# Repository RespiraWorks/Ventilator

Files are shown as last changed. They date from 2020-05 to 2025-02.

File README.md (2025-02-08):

# RespiraWorks Open Source Ventilator






</br>






This is a common repository for all hardware and software components of the RespiraWorks open source ventilator.

**If you intend to contribute, please read our [wiki](https://github.com/RespiraWorks/Ventilator/wiki) and [agreement](https://respiraworks.github.io/Ventilator/contributing/contributing.html).**

[RespiraWorks](https://respira.works/) is a 501(c)(3) non-profit organization with over 200 contributors worldwide working to design a low-cost and [open-source](open_source.md) ventilator for communities underserved by the global supply chain. Our objective is to provide the know-how and technology to enable local enterprises to manufacture and service these systems.

|           Most recent v0.4 rendering            |            Assembled v0.3 prototype             |
|:-----------------------------------------------:|:-----------------------------------------------:|
|  |  |

## Design Goals

We are dedicated to making this ventilator:
* [fully open source (software and hardware)](open_source.md)
* affordable (materials cost under US$2000)
* fully featured for extended clinical use through weaning and recovery
* vetted and filing-ready for regulatory review around the world
* optimized bill of materials to account for constrained supply chains
* designed for long-term clinical use beyond the pandemic

Most low-cost ventilator designs that have emerged in light of the COVID-19 crisis tackle the 'bridge' problem — keeping a patient alive for 6-8 hours of closely monitored care until they can be transitioned to a fully featured ventilator. We are designing that full ventilator, a highly valued medical device critical to care beyond the current crisis.

Our design shall provide essential features such as an intuitive, localized user interface, adaptive pressure- and volume-based operating modes, fine control of oxygen concentration, High Flow Nasal Cannula and other advanced features. What sets us apart from other similarly ambitious projects is our dedication to being fully open source. This repository embodies that promise.

We are targeting middle- and low-income parts of the world that will deal with COVID-19 for longer, with less access to healthcare, and a larger deficit of medical devices. We aim to deliver a design which meets the same operational rigors of current commercial ventilators, while addressing the high barrier to entry for such devices.

If you can lend your skills towards achieving this goal, please contact us at [join-us@respira.works](mailto:join-us@respira.works?subject=[GitHub]%20Join%20request). A list of roles we are looking to fill is also on our [website](https://respira.works/join-us).

## Project Status / Disclaimers

**This is an incomplete, as yet untested design that is not intended to be used on patients.**

**The repository contains live documents. There may be incomplete or contradictory information about various aspects of the design. Components may or may not connect and integrate as intended. Contents may also be out of date. If you decide to buy or build anything, do so at your own risk.**

We are currently in the process of designing our v0.4 prototype, plans whereof are captured in some of our outstanding [Milestones](https://github.com/RespiraWorks/Ventilator/milestones). The `master` branch of this repository includes bleeding edge changes in electrical, mechanical and software aspects of the project. Browse at your own peril.

For the latest stable and tested (but also obsolete) version of the design see the [Releases](https://github.com/RespiraWorks/Ventilator/releases) page.

## Repository Structure

* [**Documentation pages (outside of repository)**](https://respiraworks.github.io/Ventilator/index.html) - auto-generated pages (should eventually) include:
  * Requirements documentation
  * Regulatory documentation
  * Software documentation
  * Bill of materials for manufacturing
* [**Documentation source**](docs) - source files for the above pages
* [**System Design**](design) - describes the functional implementation and design theory of the system
* [**Manufacturing Design**](manufacturing) - describes the physical design of the ventilator and its components. Includes CAD models and notes on the manufacturing process
* [**Main Circuit Board**](pcb) - design, materials, assembly instructions for the ventilator main circuit board
* [**Software**](software) - source code for cycle controller and user interface, debug tools, and test scripts. Software architecture documentation is also here.
* [**Quality Assurance**](quality-assurance) - quality assurance strategy, testing plans, data

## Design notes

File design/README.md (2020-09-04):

# System Design

This section of the repository contains the description of ventilator design implementation and closure of issues which
apply at the system level, such as architecture configuration.

## Design Motivations

When approaching the design for the ventilator, we learned some features cannot be sacrificed if our ventilators were
to have a lasting impact for communities in need of advanced life support equipment. There are numerous avenues,
however, to reduce cost through tuning the performance specification to targeted use cases. This includes the ability
to ventilate high resistance, low compliance lungs at small tidal volumes and high respiratory rates. Our design can
significantly reduce the delivered cost of such a device by
1. reducing some performance requirements
2. developing software under a crowd-sourced model
3. not charging licensing or royalty fees.

The design has focused on a pneumatic implementation, where possible to avoid mechanical complexity (bellows, actuators,
etc), thereby placing more of a burden on the electrical and software design. This is informed by our experience that a
deep expertise of electronics is more globally prevalent than similar expertise in mechanical engineering. The device is
intended to be manufacturable by facilities that manufacture consumer electronics, automotive parts, refrigerators, or
other similar manufacturing entities near to the point of use. This approach allows flexibility in selecting
manufacturing partners who are supported from the engineering side by our globally distributed team of volunteer
engineers and manufacturing-quality professionals. To enforce this process, the design strives to identify solid supply
chain alternatives for each component and choose components that are easily sourced in our targeted regions of use,
such as Guatemala, India, Kyrgyzstan, or Nigeria.

The custom case, sensors, and valves are designed to use injection molded, laser cut, or sheet metal folded parts that
then require only basic tools to assemble, making them amenable to any number of manufacturing facilities around the
world. The chosen purchased components are readily available through global markets, including automotive supply
chains (e.g. valves and pressure sensors) and factory/warehouse supply chains (e.g. blower, tubing and pipe fittings).
The control and graphics board is designed around a custom PCB, but assembled using hand-solderable components if a
turnkey PCB supply chain were not available (though practically this would likely not be feasible from a QA perspective).

## High Level Design

The RespiraWorks Ventilator has four major subsystems with tightly
coupled interfaces:

1. [pneumatic system](pneumatic-system)
2. [electrical system](electrical-system)
3. [software system](../software/design) (documentation in code directory)
4. [mechanical assembly](mechanical) to enclose the device and provide structural support.

**#TODO:** Introduce all subsystems properly

The diagram below shows the conceptual interactions between the
pneumatic and electrical systems, with software running on both the main
controller (STM32) and a second independent graphics computer (Raspberry
Pi 3+/4) controlling the User Interface.

The following sections walk through this in more detail and explain the
basis for the design selection of various components.

Ventilator Functional Block Diagram
([source](https://docs.google.com/presentation/d/1ye96itSLfdbO9PQT0MSiq6xR2ArqD2MpV1Wj8ORfHeo/edit#slide=id.g7330d84036_1_0))



## Other Documents

* [Design rationales](design-rationales.md)
* [Concept of Operations](conop.md)
* [Systems modeling in Modelica](modelica.md)

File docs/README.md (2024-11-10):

# Documentation

The documentation created here is written in reStructuredTexT and generated using [Sphinx](https://www.sphinx-doc.org/en/master/) via a GitHub action.

## reStructuredText

reStructured text is similar to Markdown in that it is ASCII formatted text that is mostly human-readable and contains directives that specify how the text should be rendered in HTML, and other output formats.

reStructuredText is more complex than Markdown and allows for much greater flexibility in formatting as well as additional features such as *directives* that act like variables/macros that are defined once and expanded in place.

## Document Generation

The GitHub action rules can be found in `.github/workflows/docs.yml`

C++ API documentation is generated using [Doxygen](https://github.com/doxygen/doxygen)

## Variables

Frequently used values that may change can be defined in the `conf.py` file in the `rst_prolog` section. The `rst_prolog` gets including in every `.rst` file and the variables can be referenced by using the format `|VARIABLE_NAME|` which will get expanded into the generated text.

## Building the docs

Use the [docs.sh](docs.sh) script in this directory to install required dependencies and build the documentation.

To install all needed dependencies (do this once on your development machine):

```shell
./docs.sh install
```

To generate the documentation, run:

```shell
./docs.sh build
```

To render wiring harnesses only:

```shell
./docs.sh wire ./path/to/dir/or/file.yml
```

If the directories are polluted, and you want a clean slate:
```shell
./docs.sh clean
```

The generated output can be viewed by opening the file `docs/_build/html/index.html`, or you can run this script to have it open it up for you in your browser:

```shell
./docs.sh view
```

You can also check the validity of all links in all markdown and RST-generated files by running:

```shell
./docs.sh check
```

however, for this to work you must install the `lychee` tool, as described here: https://github.com/lycheeverse/lychee.
Otherwise, validity of links will be checked by CI scripts upon committing changes to the repo.

## Additional features and scripts

### Part purchasing tables

Parts catalog with links to vendors is generated by a set of custom scripts. The `json` file with parts definitions and relevant custom scripts are all maintained in [docs/purchasing](purchasing)

### Wiring assemblies documentation

Wiring assembly documentation is generated using the [WireViz](https://github.com/formatc1702/WireViz) tool. All wiring assembly definitions and relevant custom scripts are maintained in [docs/wiring](wiring).

### Traceability

We use a [traceability plugin for Sphinx](https://melexis.github.io/sphinx-traceability-extension/index.html) to generate requirement and test traceability reports.

A traceable item is defined using the `.. :item:: <id>` keyword.

By defining a traceability relationship in the target (ex. derived requirement
`:fulfills: <parent requirement id>`), and bidirectional link is created between
 the target and source `:item:`s. Traceability matrices and charts can be
 generated based on these linkages.

Over time, we can add additional attributes to the traceable items to trace data
 such as verification method, status, etc...

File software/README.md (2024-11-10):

# Ventilator Software

This directory contains the source code for the ventilator software, test code, sample data and debug utilities.

**DISCLAIMER: You should not use this on any living beings - as a ventilator, or in any other way.
These are utilities for bench testing with mechanical lung simulators only. It is also assumed that you are familiar with the software architecture and generally know what you are doing.**

## Contents

* [bootstrap](bootstrap) - initial deployment scripts for all software directly via the Raspberry pi integrated in a ventilator. Can also be used to configure a linux machine for software development or integration testing.
* [design](design) - documents on software architecture and requirements
* [common](common) - code common to both controller and GUI executables
* [controller](controller) - code for pneumatic system controller (stm32)
* [tools](tools) - controller debug client and other tools for calibration, configuration and testing
* [gui](gui) - code for the ventilator graphical interface (Qt)

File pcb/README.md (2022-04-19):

# Ventilator Mainboard 

This directory contains files for the Ventilator mainboard design.



The RespiraWorks Ventilator Mainboard PCB is a custom component that integrates the Cycle Controller, UI Computer,
sensors, actuator drives, power supplies, filtering, and protection components.

Due to the coupled nature of the controls, electrical, and mechanical components and their design the RespiraWorks
ventilator contains a custom fabricated printed circuit board (PCB) to connect the microcontroller, interface processor,
and sensor interfaces. The use of a custom PCB greatly reduces the chance for electrical assembly and fabrication errors
and is far more amenable to a quality fabrication process than hand-soldered components. We do not intend for this
component to be hand-assembled, and engineering turnkey fabrication instructions have been generated as part of the
submission; no assembly instructions are provided here.

The original Rev 1 PCB was done in Altium.  As of Rev A, this project has moved to KiCad for better accessibility.

## Rev A

The latest revision of the PCB is Rev A, designed to be used in the top-level design revision Ventilator v0.4.

The main design is in this folder and the project file is here: [Ventilator Mainboard Rev A](Ventilator.pro)

Recently exported files for PCB manufacture can be found on our Google Drive at
[Manufacturing/Output files v0.4/PCB](https://tinyurl.com/2p8af3fm).

This revision integrates many of the modules and daughter-cards in PCB Rev 1.0 into a single PCB, while breaking out the sensors to daughter-cards to make it better adaptable to sensors available in other markets.  It adds some important new features:
 - Moved CycleController from STM32L452 to STM32L496 microcontroller for more I/O pins, memory, and storage.
 - Added an independent FPGA-based supervisor.
 - Higher power capability now up to 120W.
 - Self-powered power loss alarm.
 - Integrated stepper drivers.
 - Ambient pressure sensing for altitude compensation.
 - Real time clock capability.
 - EEPROM for storing calibration data.
 - Additional pressure sensor channels to enable nested flow control.
 - Temperature sensors to monitor component health.
 - Integrated Li-Ion battery backup, charging, and monitoring.
 - Additional power connections for display, fans, and indicator lights.

## Sensor daughter-boards

> TODO: add documentation about these

## Rev 1.0

An archive of the previous version of the PCB, including the Altium-based design project and a snapshot of the old
readme is available on our Google Drive at
[Manufacturing/Output files v0.2-0.3/PCB](https://drive.google.com/drive/folders/1xHPLvo59tGI5uU38FrWMkVGmK_UR2sjQ?usp=sharing)

## Current issues

Issues for PCB work are tracked by tickets with the [PCB label](https://github.com/RespiraWorks/Ventilator/labels/pcb).

Somewhat related are the [Electrical design](https://github.com/RespiraWorks/Ventilator/labels/Electrical) issues.

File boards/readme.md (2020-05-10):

This directory holds the board file used by platformio to build the stm32 controller software.

The board file (custom\_stm32.json) was copied from the platformio board file nucleo\_l452.json .platformio/platforms/ststm32/boards/nucleo\_l452re.json

The main difference being the removal of the variant line to prevent platformio from including the stm32 supporting HAL.

Additionally, a few additional files related to the stm32 build have been added to this directory as a convenient place to keep them:

stm32\_ldscript.ld - This is the linker script copied from: \~/.platformio/packages/framework-arduinoststm32/variants/NUCLEO\_L452RE/ldscript.ld with some minor changes such as removing the heap (not used) and stack (defined in the HAL cpp file).

stm32\_scripts.py - A short Python script used by the platformio build to add some linker flags that can't be added in the platformio.ini file.

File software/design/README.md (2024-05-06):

# Software Design

The RespiraWorks ventilator includes software running on two computers:
an STM32 microcontroller and a Raspberry Pi.

Module diagram

The microcontroller runs bare-metal and controls the sensors and
actuators (valves and blower).  Its main loop runs every
10ms on a hardware timer interrupt,
and the code running in the main loop contains no loops of variable
length, ensuring minimal jitter. The microcontroller’s software is
written in C++.

The Raspberry Pi runs Linux and is used for displaying the GUI. The
software we wrote is a Qt app, also written in C++. The app displays a
GUI on the ventilator’s touch screen, showing sensor data received from
the controller. Users set high-level parameters via the GUI (e.g. "PIP
20 cmH2O"), and then the GUI software commands the controller to meet
these parameters. The GUI software is also responsible for calculating
alarms and readings derived from raw sensor values (such as measured
PIP/PEEP).

We chose to use two separate computers for three reasons.
1. Two computers reduces the amount of software that is immediately hazardous
to the patient. Since our UI code runs on a separate device with no
direct access to the ventilator’s actuators, a bug or crash in it is
less likely to cause immediate harm; the ventilator will just keep
running with the most recent parameters (and, in the future, sound an alarm).
2. This design saves time and money because it allows us to use
large libraries like Linux and Qt, which make it easier to develop the
GUI, but would likely be unacceptable in a patient-critical module like
the cycle controller.
3. Having two modules adds a level of
redundancy. If the microcontroller crashes, it will immediately receive
new commands from the Raspberry Pi, and the Pi can raise an alarm.
Similarly, if the Pi crashes, the ventilator continues running with the
last set of parameters, and the cycle controller can raise an alarm.
(Disclosure: Neither of these alarms is currently implemented, and we
have not performed extensive testing of this failure model.)

Like the rest of the RespiraWorks project, our software is developed in
the open on GitHub. We have an extensive continuous integration
infrastructure running unit tests on x86, and we are building
infrastructure to run automated tests on the full device. We are also
nearly ready to start testing our software against a Modelica simulation
of the device. We hope this will make it easier for developers who do
not have access to hardware to contribute to the project. We also
believe having a robust simulation environment will allow us to run
tests that would otherwise be prohibitively time-consuming, for instance
running each commit against many combinations of ventilator parameters
plus lung compliances.

Besides a detailed user manual and maintenance plan, the device will also
come with a robust self-test mode.  This ensures that produced
ventilators achieve necessary safety levels before they are used with
patients and will allow users to check the health of the device over its
lifetime. A cryptographic hash will be released with the approved
software, and allow local manufacturers to be confident in the software
they are loading to the device.

## Communication Between Pi and Microcontroller

The microcontroller and Raspberry Pi communicate over a serial bus using
a simple, predictable protocol. Every ~50ms, the microcontroller sends
its current state to the Raspberry Pi, and every ~50ms, the Raspberry
Pi sends its full state to the microcontroller.  There are no ACKs,
resends, detection of missed packets, etc.

This simplified communication protocol avoids failure modes present in
other protocols.  For instance, imagine a different, stateful protocol
where one command the GUI can send is `set PIP to X`.  Suppose the GUI
sends two packets, `set PIP to 15` and `set PIP to 20`, and imagine that
the first one gets corrupted or lost on the wire.  The controller must
not accept the `PIP 20` command until it receives and applies the `PIP
15` command, otherwise the final PIP will be 15!  This requires buffers,
resends, and complex logic that, in the limit, looks much like a full
implementation of TCP.

Our design sidesteps this whole class of problems. If a message gets
missed or corrupted, we can just wait for the next one.

The state is encoded for transport on the wire using protocol
buffers (specifically, nanopb) and
wrapped in a frame with a checksum for detecting packet corruption. As
compared to a fully custom binary format, this makes it far easier to
change the protocol and potentially interoperate with other systems.

## Software component architecture

[Controller architecture](controller_architecture.md)

[GUI architecture](GUI_architecture.md)

## Other documents

There is a document defining the [ventilation modes](ventilation_modes.md) we intend to support.

## Testing considerations

There is a strategy defined for [embedded software testing](embedded_software_testing.md).

## Milestones

We have completed and successfully demonstrated the
[Alpha Milestone](milestone_alpha.md) and the [v0.2 milestone](milestone_v0.2.md).

## Design Reviews

**TODO:** Links to the design reviews

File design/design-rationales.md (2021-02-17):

# Design Rationales

NOTE: The documentation below is a summary and may be out of date.

## Overview

This file is meant to document the rationales for the design decisions we're making - or things we considered and rejected.

Caution: this document has not been formally reviewed and is a work in progress. Be responsible to
understand the provenance of documentation.

Also note: right now we are collecting initial information here since it is easier - we may split
this up to have the different sections live with the different component folders, but we'll figure that out later.

## Guiding Principles

1. **Low cost but robust and safe** - we want to create something that is affordable, but also that can perform the
necessary duties reliably with high confidence over extended periods of time. The goal is to satisfy external
specifications for ventilator requirements - but also assess the cost of the requirements and not blindly follow them if
it drives big decisions in the system.

2. **Keep It Simple (Stupid)** - remove complexity wherever possible to reduce failure modes (and cost), without
sacrificing key functionality (though certain functionality may not be achieved)

3. **Make it something that doctors will use** - it won't necessarily do everything, but we want the ventilator to
provide the key needs of doctors. Therefore, we must keep doctors extremely in the loop and constantly get feedback from
them on what we're doing.

4. **Amenable to developing world supply chains and maintenance** - don't presume that the medical context we might be
used to is the same in our target market. The only way to get this information is contact with doctors and workers
familiar with the facts on the ground.

5. **Open source** - we want this project to be something that anyone who wants can build off of and leverage.
Therefore, all designs, rationales behind those designs, requirements, processes, etc. will be documented in a common
repo that everyone has access to. **#TODO** - go through and make sure all of the links in here are in git so that
people can access them (some slack links exist temporarily before the information is fully resolved and moved to git).

## System CONOPS/System Design

More detailed thoughts on this [here](conop.md).

* Targeting **pressure control** for two reasons:
    1. We got early feedback that this was most important to doctors - though we have gotten feedback that volume
       control is also important.
    2. A lower cost pressure controlled system seemed more achievable - and theoretically a good pressure controlled
       system should be able to do volume control. Currently we are pursuing pressure control and will be evaluating how
       accurate volume measurements we can get to determine if the design can also support volume control.

* **Doctors need fine control of FiO2** -> this drives the need for an oxygen supply, the need to support oxygen mixing
and sensing, and the need for a variable state valve on the O2 supply to adjust the flow rate dynamically.
**#TODO** Need more info on the ox system design we pick.

* **Multiple closed loop (feedback control) systems create complexity by creating interacting dynamics** -> we're
attempting to only have a single closed loop controlled part of the system at a time and to target one key feature (e.g.
pressure with FiO2 achieved across cycles). We're also working to determine which components (e.g., valves, blower) need
to be controlled and how in order to figure out what will actually support the system requirements.

* Anything that will be exposed to high oxygen concentrations and pressures needs to be safe and ox-clean. This drives a
desire to **reduce the number of items directly in the flow as much as possible**, especially for high-pressure (greater
than 1 bar O2)

* **Air valve after the fan/blower with air valve being closed loop controlled and fan being open loop** -> The
ventilator requires a high rise time of the pressure when transition from PEEP to PIP. A motor which can change the fan
inertia this quickly against increasing pressure ends up being the fan for some high-performance ventilators, or
expensive. We have solved this by the use of a proportional valve after the fan. The fan runs at constant power, and the
pinch valve is used to modulate the flow. For reference, one fan we got quoted was $500 and we were never able to get one
delivered. A fan capable of meeting the pressure spec + an air valve capable of the rise time spec was less than $75.

* The goal is to maintain **some bias flow through the system at all times**, both to help the fan and to avoid big
surges from completely opening and closing different parts of the circuit. This also helps ensure a 'one way' flow of
particles and aids with sterilization.

* **Trigger breath transitions off of changes in flow instead of pressure** -> Because the ventilator is pressure
controlled, it adapts to small changes in pressure by adjusting the flow rate (by adjusting the valve states) in order
to maintain pressure. Therefore, changes in flow rate are a better sign that the patient is attempting to inhale or
exhale. **#TODO** need to confirm this/flesh this out as we go

* **Anti-asphyxiation design** (**#TODO** need to confirm all this)
    * **Pneumatic** If the ventilator loses power, it is important that the patient is able to breathe and is not given
      dangerous amounts of pressure/flow. The oxygen system is fed by an external pressure source that the ventilator
      doesn't control; therefore, in the loss of power it is important to shut off flow from the oxygen system to keep
      the patient safe. We accomplish this by using a normally closed solenoid on the oxygen limb. The air/blower valve
      and the exhale valve are made to be normally open so that those paths are unobstructed to allow the patient to
      breathe.
    * **Electrical** To support the air/blower valves and exhale valves being normally open, the Cycle Controller
      watchdog timer is connected to the stepper motor drivers, which will default them to an unpowered state in the
      event of a Cycle Controller computing failure, causing the valves to snap open.

* **Use of stepper motors** - **#TODO** need to fill this out

* **Metric vs imperial** - **#TODO** fill this out when we make a decision

## Valves

* **Pinch Valve (Custom design)**
    * Low cost, robust design for achieving variable flow based on peristaltic tubing.
    * The valve mechanical components are not exposed to the flow, which means it is not exposed to high O2
      concentrations directly.
    * Normally open, which is important for anti-asphyxiation in the case of power loss
    * Still evaluating fatigue and lifetime / sealing.
    * Originally designed as the exhale valve to give control for maintaining PEEP - under considering to use for both
      the air inlet and for the oxygen inlet
    * For more informatin about the design of this valve, see [here](../manufacturing/internals/pinch_valve)

* **Idle Air Control Valve (IAC)**
    * Common automotive part that is cheap and widely available.
    * A linear stepper motor drives a pintle up and down to create a variable orifice.
    * Unclear how these valves perform in high O2 environments or if they could be sufficiently rated/cleaned.
    * Significantly cheaper, more robust, and more widely available than the pinch valve.

* **Proportional Solenoid (PSOL)**
    * Relatively uncommon part but used in traditional ventilators.
    * Provides precise, reliable control of high-pressure gasses.
    * May be cost effective but requires a high-pressure source of oxygen (can not use low pressure sources like oxygen
      concentrators without a booster pump).
    * O2 cleaned PSOLs are relatively hard to find, though are already in use on ventilators. We may be able to clean
      automotive PSOLs.
    * Normally closed, which is important for anti-asphyxiation. **#TODO** need to confirm this

* **One way valve (check valve)**
    * Needs to work in an O2 environment
    * Needs to be reliable and relatively low cost
    * Still figuring out the exact one way valve design
    * Two possibilities are a normal umbrella seat check valve, problem is these have a high cracking pressure. This
      could be OK on the intake side where the fan can generate this but would be a problem on exhale.
    * duckbill valves have also been explored, but these can chatter at low flow rates.
    * Could possibly modify a normal check valve by cutting the spring down or out.

* **Relief Valve**
    * **#TODO** when we figure this out

## Tubing
* Pick peristaltic tubing in the pinch valves so that it can withstand many cycles
* Otherwise any biocompatible tubing is fine, gneerally Tygon for most of the testing.
* Needs to be O2 safe
* 3/4 inch standard allows relatively cheap fittings. Need to transition to metric for int'l.

## Sensors

* **DP sensors / Venturi**
    * The goal of the venturi design is to measure the flow through the system at a limited pressure drop and with a
      large signal.
    * Venturi's are nice because they are cheap and yet can provide reliable flow measurements. See
      [this ticket](https://github.com/RespiraWorks/Ventilator/issues/9) for info about evaluating the venturi's.
    * Currently we are using the difference between the two flow measurements (one for inhale and one for exhale) to
      determine the tidal volume delivered to the patient. We are still evaluating how to do this - see
      [this ticket](https://github.com/RespiraWorks/Ventilator/issues/57) for more information.
    * Another open questions is manufacturing of the venturis - currently the goal is to design a venturi that can be
      injection molded.
    * For more informatni about the venturi design, see [here](../manufacturing/internals/venturi).

* **Patient Pressure sensors**
    * Needs to be reliable, handle many cycles, and meet the required ranges and accuracies of the requirements
      (**#TODO:** flesh this out more).
    * Currently only one sensor is used, but maybe a second one is required for reliability.

* **O2 sensor**
    * The O2 sensor needs to be able to measure up to 100% O2
    * Right now we are using a galvanic cell O2 sensor - but those are known to degrade quickly.
      [This ticket](https://github.com/RespiraWorks/Ventilator/issues/56) is tracking our discussions on this topic.

* **Mass flow sensor***
    * We have shied away from mass flow sensors because they are very expensive when compared to the DP sensor/venturi
      design. However, they are accurate and used on other system so they are not completely ruled out.

## Filters
* Filters on inlet/outlet to prevent contaminents from the surrounding environment getting into the device
* Filter on patient circuit to avoid device contamination and spreading particles between patients
* We're currently looking at HEPA filters since they are commonly avaible and cheap - but we're also evaluating other
  options. HEPA filters are appropriate because they are designed to filter small particles.
  [More info on HEPA filters](https://ntrs.nasa.gov/archive/nasa/casi.ntrs.nasa.gov/20170005166.pdf)
* 2 part mold for holding the filters is meant to be easily manufacturable and to allow easy changing of the filters
  over time
* Filters are placed physically on the outside of the box so they can be replaced without the box being opened

## Blower
* Current blower is not rated to 100% O2, which drives the lack of a blower on the O2 system and a one way valve in
  front of the blower to keep it separate from the high O2 part of the system.
* We have evaluated a large number of blowers. When balancing supply chain, ubiquity of specification, and future
  availability, we settled on this one. However, there is an issue with the pressure spec for the fan. If we needed to
  reach 60 cm H2O, this fan might be under powered. We are currently leaning to not support those high pressures
* **#TODO:** link to the fan we picked

## Enclosure
* Must be sterilizable
* Must be manufacturable with commonly available fabrication equipment in the markets we are assessing (currently
  targeting custom folded sheet metal)
* Enclosed to protect the internals and keep out dust
* Has an external fan for cooling the internal electronics
* Ruggedized and compatible with the hospital environment
* Must support easy assembly and maintenance of the various components

## Humidifier
* Currently planning to use an off the shelf external humidifier—see [this ticket](https://github.com/RespiraWorks/Ventilator/issues/704) for more details.

## PCB/Electronics

* **SRM32 Microcontroller For the Cycle Controller**
    * More powerful than the simpler arduino and Raspberry pis, but still cheap and widely available
    * Used in other medical devices
    * Comes with more powerful/extensive debugging tools
    * Familiar to many of the members of our team
    * See [this ticket](https://github.com/RespiraWorks/Ventilator/issues/709) for more details on why a STM32
      microcontroller was chosen.
* **Rasperry PI and Rasperry PI Touch Screen for GUI**
    * Cheap and widely available
    * Existing libraries for touch screen interactions that can be leveraged
    * Has lower performance requirements than the cycle controller
* **Power Supply**
    * 12V standard chosen to ensure flexibility of power supplies (e.g. battery or UPC)
    * Open question on internal alarms battery
* **#TODO** - need more here.
* **#TODO** - add diagrams from design reviews and such

## Software

* **#TODO** - add diagrams from design reviews and such
### Separation of UI Controller and Cycle Controller
* To maximize safety, it is important to minimize the amount of software that is immediately hazardous to the patient
  (can cause harm in <1s, making human intervention useless), and expose any hazardous software to high levels of
  verification and testing. By moving the UI code to a separate porcess, it reduces risk and saves time because the
  complicated UI code doesn't have to be exposed to the same verification and testing as the cycle controller.

* NOTE: Neither of the controllers are a complete backup for the other - this is not a redundant system.  If either
  fails in a way that is not fixed through the watchdog reset, an immediate intervention will be needed to keep the
  patient alive.  The objective in the case of either failure is to sound the alarm so that the intervention can
  happen - and to design the system such that in the event of a failure there is time to make an intervention.  Making
  a truly redundant system will add cost and time, and so has been deferred for now.

* **Watchdog Timers**
    * In the event of a computing failure in either the UI Computer or the Cycle Controller, a watchdog timer monitors
      each and will reset the offending computer, which should then be able to regain control of the valves.
    * **#TODO** it will need to be confirmed in the final design that the UI Computer cannot command any modes that will
      cause the Cycle Controller to hold these valves closed.

### GUI / UI Controller
* **#TODO** - needs more
* Items that fall within the UI Controller:
    * Cycle Controller Watchdog/Alarm
    * User Parameter Setting
    * Ventilation Mode Setting
    * Sensor Data Reporting
    * Respiratory Cycle Plot Display
    * Alarm Information Display
    * Alarm-specific alert sounds

### Cycle Controller
* **#TODO** - needs more
* Items that fall within the cycle controller:
    * UI Computer Watchdog/Alarm
    * Closed-Loop Valve Control
    * Open-Loop Blower/Valve Control
    * Respiratory cycle Control
    * Sensor Data Reading
    * Sensor Failure Alarm
    * Overpressure Alarm
    * Respiration Rate Alarm
    * Broken Loop Alarm

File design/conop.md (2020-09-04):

# RespiraWorks Ventilator Concept of Operations (conop)

## Purpose

- Build a common understanding of ventilator internal operation amongst different parts of the team.

- Caution: this document has not been formally reviewed and is a work in progress. Be responsible to understand the provenance of documentation.

## Document Content

- Summary of key constraints
- Understanding of current intra-breath cycle control for the development ("Pizza") board.
- Preliminary description of system operation for next iteration of system with O2 mixing
- Envisioned Inter and Intra-breath cycle control states
- Open questions / points to resolve.

## Functional Diagram

Functional Block Diagram

## "Pizza Build" Intra-breath Cycle Control

The Alpha system flow path is:
- Fan
- Air Valve (not on current pizza build)
- Tee <-> Test Lung
- Exhale valve
- Exhaust

The Alpha build (first iteration) did closed loop control on the blower speed and setpoint control on the exhale valve state to achieve the desired target pressure. However, this left significant shortfalls in both pressure rise and pressure reduction times.

The intra-breath control cycle for the Alpha build is:
- **Inhale:**
    - Increase pressure set point for closed loop control to PIP pressure
    - Exhale moves to exhale position (fully closed)
    - Controller adjusts blower speed based on PID control closed around the measured patient pressure
    - PIP pressure target is maintained for a specified amount of time - then step transition to exhale
- **Exhale:**
    - Exhale valve moves to exhale position (fully open)
    - Controller adjusts pressure set point for closed loop control to PEEP pressure
    - Controller adjusts blower speed to meet PEEP.
    - PEEP pressure target is maintained for a specified amount of time - then transition back to inhale

Alpha build has no inter-breath or "adaptive" control on top of this.

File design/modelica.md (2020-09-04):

# Modelica Simulation Model

## Modelica Overview

Modelica [www.modelica.org](http://www.modelica.org)
is a non-proprietary, object-oriented, equation-based language used to model complex multi-domain physical systems.
Developed by the non-profit Modelica Association, the Modelica language is widely used in industry for modeling physical
systems with mechanical, electrical, pneumatic, hydraulic, thermal, control, electric power, and process-oriented
components.  With Modelica, models can be built from the open source Modelica Standard Library (the largest free library
for multi-domain models), other open source libraries, commercial libraries, and custom in-house libraries to leverage
existing modeling technology while providing the openness and flexibility to incorporate custom modeling IP.

Modelica is used for modeling the dynamic behavior of technical systems.  Models are described by differential,
algebraic, and discrete equations.  Modelica physical models are acausal and allow the creation of reusable primitive
components, subsystems, and complete systems.  To illustrate a simple Modelica model, the figure below shows the
graphical representation and Modelica code for the 1D rotational inertia from the Modelica Standard Library.  Modelica
models are written as equations, typically in standard text book form, that express relationships between variables.
Since Modelica models are descriptive but not necessarily programmatic, a Modelica tool is needed to generate executable
code.  The entire process starting from Modelica code to a simulation result is shown in the figure below. A Modelica
compiler assembles the Modelica code, performs symbolic manipulation on the equations, generates C code, and compiles
the C code into a simulation object that is linked with a numerical solver that executes to generate the simulation
result.  Both open source and commercial compilers are available for Modelica.  With the powerful symbolic processing
from a Modelica compiler, modelers are free to focus on developing high quality models for systems engineering rather
than numerics and equation solving.

## Model Overview

For the ventilator work, we partnered with Modelon, who provided licenses for a beta version of their commercial
Modelica tool Modelon Impact [https://www.modelon.com/modelon-impact/](https://www.modelon.com/modelon-impact/).
Modelon Impact is a fully featured Modelica development and simulation environment integrated into a web browser.
Modelon Impact is designed to enable system simulation beyond just CAE experts and facilitate collaboration and
model-based engineering.

Modelon helped us to develop a package of models to support the ventilator physical system and controls development.
These models are based on Modelon's Pneumatics Library, a commercial library for modeling pneumatic systems.  Modelon
continues to develop the ventilator modeling package in partnership with RespiraWorks.

As shown in the figure below, there are three main parts of the model: the controller, the ventilator, and the patient.
The beauty of modelon impact is that it lets you easily swap in different instances of each of the components and see
how that affects your results. Below we'll walk through how each of these were created.

Screenshot of Modelon Impact Showing The Model GUI



### Patient

There are currently three main different patient models. The first is a basic model that allows the user to specify a
resistance and compliance and then calculates the internal volume and pressure based on pressure and flow rate from the
ventilator. The second is a breathing model that allows a respiratory rate, IE ratio, and a musculatory pressure to be
specified, controlling both how quickly and how forcefully the simulated patient breathes. There is also a more advanced
lung model that incorporates more parameters to enable more complex simulations, though we have not used this model
extensively yet.

### Ventilator



 Current Ventilator Model in Modelica

As the ventilator design has changed, there have been many iterations of the ventilator model in modelica. The most
recent one is shown in the figure below, where you can see the oxygen leg with oxygen source and ox valve, the air
inhale branch with blower and pinch valve, the patient circuit with venturis before and after, and the exhale leg with
the exhale pinch valve. The control signals from the controller enter through the control bus at the top and are then
routed to the actuators (blower and 3x valves), and the pressure measurements are passed back to the controller through
the same control interface.

Each component is built up using the modelica language. The components in this ventilator model are a combination of
default modelica components and components created specifically for our ventilator. The blower component, the
proportional pinch valve components, and the oxygen valve components are based on test data and data sheets for the
actual hardware we are using. An example of the flow curves inside the modelica model for the custom proportional pinch
valves are shown below. Similar curves were created for the blower and the oxygen valve.



Flow Curves for Custom Proportional Pinch Valves Used Inside Modelica, Based on Flow Testing. Valve flow vs opening
command with different curves for DP across the valve.

### Controller

We explored two different ways of implementing a controller in Modelica. The first was to build the controller in
modelica, using components based in the modelica language. The second is to write a controller outside of modelica
(e.g. in C++) and to then link it through the modelica interface. The first approach allows rapid interaction for those
who are less familiar with how to implement controllers in software; this allowed us to prototype different controller
configurations before we actually had the hardware set up to test them with the real system. The second approach could
be useful for testing the controller software without being constrained by hardware, something that is discussed in the
next section.

### Executing The Model

When the model is run, the various components begin in their initial state. The tool then steps forward in time,
calculating both the commands from the controller and the corresponding response of the system at each time step,
solving the various underlying equations to calculate pressures, flow rates, etc. The results can then be visualized to
see how the system performed over time.

## Comparing Model to Hardware

Currently, we are working to verify that the model matches what we see with hardware. This has been challenging for a
few key reasons:

*   Rapidly changing controller code that hasn't been integrated into the modelica model. This makes it difficult to
    tell if differences between results from the model and the hardware are because of issues in how the hardware is
    modeled, or differences in the commands coming from the controller, which affects the system response.
    Unfortunately, the structure of the controller code has also been changing, which means that this isn't completely
    solved by using the external controller.
*   Rapidly changing hardware that has not been completely characterized. As we iterate on the hardware design, we have
    been changing components faster than we've been able to collect characterization data with which to anchor our
    modelica models.

Moving forward, we are evaluating ways to anchor the modelica model to give us more confidence in its predictive
capabilities.

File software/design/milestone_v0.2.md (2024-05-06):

# This milestone is complete

_Information below only for posterity._

## How to use this page
This is a high-level overview of what we want to achieve for v0.2 (a.k.a Covent) milestone. Up-to-date state of its implementation
is [here](https://docs.google.com/document/d/1CHgz-y6wV6duTg66s1h8-wZZ6Tn22U1iL5WtjhSYQgk). Requirements are captured on Valispace.

## Date

Deliver to Covent by June 18th.

# Objectives
## Modes
 1. Pressure Assist Mode. That is mandatory ventilation together with inspiratory attempt detection.
 2. (stretch goal) High-flow nasal cannula (HFNC). Ventilator provides light continuous positive pressure, patient breathes on their own.
 3. (stretch goal) Pre-test mode (a.k.a. self-test mode).

Full description of all ventilator modes is [here](ventilation_modes.md).

## User Interaction

See [UI Requirements](UI_requirements.md).

## Alarms
We need 6 alarms that were in covent requirements:
1. Gas pipeline failure
2. Pressure exceeds
3. Apnea
4. Pressure not achieved
5. Tidal volume
6. Electricity supply failure

## GUI
Two new features have to be added for Covent:
1. Modes selection
2. Alarms settings

# Requirements

Requirements are captured in Valispace, tag v0.2

# Tasks
Specific tasks are captured as GitHub Issues in the following milestones:
 - [v0.2 GUI](https://github.com/RespiraWorks/Ventilator/milestone/12)
 - [v0.2 Alarms](https://github.com/RespiraWorks/Ventilator/milestone/11)
 - [Pressure Assist Mode](https://github.com/RespiraWorks/Ventilator/milestone/8)
 - **HFNC mode** - deleted milestone (August 2020)
 - (stretch) Self-test mode - deleted milestone (January 2021)
 - (stretch) [v0.2 Controller](https://github.com/RespiraWorks/Ventilator/milestone/13)

# Brain dump, to be sorted and reorganized into sections above

We also need:
* Architecture / preliminary design review
* Calibration tools/modes for subsystems
* Validation testing plans for specific subsystems (this might be software or additional documentation overhead)
* Listing and managing the software-specific risks (note: this work is underway [here](https://docs.google.com/spreadsheets/d/1p26b3XyhEte8BvnE9otj118MW5ajGM21dGfTXldG8sM) by jam@)
* We need a software architecture review
* We need 1 or 2 people to help physical design team publish their content on github and document things in a colleague- and people-friendly way

Specific software designs needed:
* A design for alarm management ([Slack thread](https://respiraworks.slack.com/archives/C0100SF3N5T/p1589153203185000))
* A design for controller self-test mode ([Slack thread](https://respiraworks.slack.com/archives/C0100SF3N5T/p1589153203185000))
* Persistence (what to do if controller resets - start from blank slate? recover control state?)

## Robust testing and debugging
* A debugging interface - ability for developers to debug what's going on in more detail than the user-facing GUI provides
* Continuous Integration that runs tests on a real device:
  * Running unit tests against a device - which is also critical for validating the correctness of the HAL
  * Running integration tests against a full ventilator assembly
* Continuous Integration that builds a GUI image for RPi

## Simulated testing

We need simulated integration testing of physical scenarios such as "patient is hooked up" etc.

We have a sub-team of folks from Modelon who hang out on [#modelica](https://app.slack.com/client/T0102KRCH5M/C011HUP75EJ) and build a model of the system (ventilator + patient + controller) in Modelica, a language for simulating physical systems. We want to integrate our Controller with that model so we can simulate what would happen if the real ventilator was being controlled by it. See [these meeting notes](https://docs.google.com/document/d/14lrTVcYuuUii7QTvuJJneex-_uKSHQ33Hg9CR5pOARo/edit#heading=h.cpwphjtw2hj8) for more.

Can we check in regularly against Modelica to gain confidence that we're meeting functional requirements?

Contact persons:
* On Modelica side, John Batteh and Elizabeth Hillstrom.
* On Software side, Eugene Kirpichov

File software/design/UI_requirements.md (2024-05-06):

# User Interface Requirements

The UI runs on a 1024x600 touchscreen. There are no external buttons or anything.

The UI requirements below come from several sources:
* Original mock-ups (the black-and-white mockups included
  [here](https://www.ics.com/blog/ics-joins-respiraworks-on-ventilator-project))
* [ICS prototype](http://demo.ics.com/ventilatorui-demo/) that was built based on the mock-ups
* [This paper](https://ccforum.biomedcentral.com/articles/10.1186/s13054-016-1431-1) and
  [this demo](https://www.youtube.com/watch?v=BT3snJ1Hm2s)
* [These notes](https://docs.google.com/document/d/1QFFcg2gL3PXXzyqgSBz3XZQm_oobZ2osFuErh492UEA/edit) from a
  conversation with a respiratory therapist

The list below is incomplete and possibly wrong in some ways.
Please consult SRS [Requirements page](https://respiraworks.github.io/Ventilator/software/SRS.html).
However, Valispace also does not have complete information at the time of writing. Proceed with caution.

## Self-test mode

On startup, ventilator is in self-test mode. It performs a set of checks and reports on the status.

Some checks are **automatic** _(eg that a certain tube is not blocked: turn on the blower, check that output flow
sensor detects some flow)_, Some are **manual** _(eg for "the buzzer works" it needs to turn on the buzzer and ask user
whether it's audible)_

The **full set of checks** is not yet known and generally open-ended.
Checks should include **guidance on how to fix** if it failed.
The self-test mode should be easy to use _(the hospital where the therapist above works decided not to purchase vents
where it was too cumbersome)_.
Results of self-test should be retained in memory.

**Open questions:**
* Should you be able to perform self-test only on startup or at any time?
* Should you confirm that patient is not connected?
* Should device refuse to operate if a check fails?

See also https://github.com/RespiraWorks/Ventilator/issues/307.

## Ventilation modes

We intend to support **Command Pressure** _(device commands all breaths)_, **Pressure Assist** _(device detects inhale
effort and helps that breath, but also initiates breaths if patient doesn't)_, **CPAP with O2 therapy aka HFNC** _(light
constant positive O2-saturated air pressure, non-invasive)_.

_Note: Different sources seem to indicate that pressure-controlled modes are going out of favor and volume control is
preferable (regular - not PRVC or VC+) - eg see
[notes](https://docs.google.com/document/d/1QFFcg2gL3PXXzyqgSBz3XZQm_oobZ2osFuErh492UEA/edit). But for v0.2 we're doing
pressure control._

**Mode parameters**: Each mode has several parameters defining it, e.g. Respiratory Rate, PIP (Peak Inspiratory
Pressure), PEEP (Positive End-Expiratory Pressure), FiO2 (O2 percentage). Parameter changes must be confirmed before
taking effect.

**Displayed measurements**: In each mode we display real-time graphs and sensor readings of several measured values:
pressure, flow, volume.

**Measured vs. commanded values**: All or almost all values have a "commanded" and "measured" value. E.g. ventilator
tries to achieve a certain PIP - this is the "commanded" value - but what it actually achieves is the "measured" value.
If they're too far off, this is bad and usually triggers an alarm.

## Alarms
**Alarm formats:**
* https://docs.google.com/document/d/1bMZfkq_p8dkg7F0ZGVIFhityv-s3GVRMsm_Nd1zNlww/edit#heading=h.yvoratpyj4xl
* Specifies visual flashing frequency / duty cycle
* Specifies auditory pulse frequency / pattern
* Derived from 60601-1-8

**Alarm conditions:**
The main alarm types for v0.2 are **"measured value too far from commanded value"** and **"the device is in a bad
state"** _(eg some tube disconnected, battery low etc)_.

Consider a **"check settings"** alarm. Per
[notes](https://docs.google.com/document/d/1QFFcg2gL3PXXzyqgSBz3XZQm_oobZ2osFuErh492UEA/edit) drs check settings every
3-6 hours, so maybe we should issue a low-prio alarm if settings haven't been confirmed in longer than that.

**Alarm presentation:**
* Alarms are indicated visually and sometimes audially (buzzer, continuous tone).
* A good way to display the "measured value off" alarm is to color the wrong value's background.
* At any moment the GUI must display the highest-priority alarm.
* You should be able to see all active alarms

**Alarm priorities:** low, medium, high (buzzer), and one or two alarms emit a continuous beep.

**Alarm lifecycle:**
* The alarm becomes active when its condition is met.
* Open question: We haven't figured out a general rule for when an alarm stops being active.
* Alarms can be suppressed in several ways: eg. cancel a particular alarm _(we don't know exactly what this means)_,
suspend all audial alarms for 2 minutes, etc. (see `01_Alarms` in Valispace)

**General advice:**
* Alarm fatigue is real. Need to make alarm management simple and conductive towards minimizing fatigue.

**Additional alarms per ISO 80601-2-12:**
(See [Slack thread](https://respiraworks.slack.com/archives/C011UMNUWGZ/p1591500042061800?thread_ts=1591207530.031400&cid=C011UMNUWGZ))


## Event logs (not in v0.2)

GUI must include a way to view the event log. It must include:
* All alarm-related events (activated, cancelled etc)
* Confirmed parameter changes and mode changes

## Non-functional requirements
The screen resolution is 1024x600.

**Remote observation/control**
* Things must be **visible from a distance of N meters**. The Covent reqs say from 1 meter, but per
[notes](https://docs.google.com/document/d/1QFFcg2gL3PXXzyqgSBz3XZQm_oobZ2osFuErh492UEA) drs often want to observe
the screen from outside the patient's room, to decrease exposure to infection.
* Nice-to-have: remote control - also to decrease exposure.

**Usability:**
* Errors can kill a patient, and the UI is used by overworked staff. It is very important to design for minimizing
  chance of human error and minimizing dr fatigue.
* Staff in target markets where there's no vents will be inexperienced with vents. UI should help them, eg understand
  the numbers, guide towards configuring things right.
  * Example: in volume-controlled modes, there's an ideal volume of 4-8mL per kg of ideal body weight (based on
    gender/height). Could set default volume by that and color-code if setting outside this range.

Consider the likely working conditions - need a dark theme (optionally light theme too).

The UI should be colorblind-friendly, at least for elements where discerning the color is safety-critical.

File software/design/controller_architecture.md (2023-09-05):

## Cycle Controller

Our cycle controller runs on an STM32 ARM chip and is written in C++17.

For more details on the inner workings of the controller, see
[Controller description](https://docs.google.com/document/d/1hztIBu9DR52r0LQuIpt6DZByBLfXfJy21BGqk2F34g8).

**TODO:** Migrate contents of the above document to github.

There is a
[Circuit board ICD](https://docs.google.com/spreadsheets/d/1JOSQKxkQxXJ6MCMDI9PwUQ6kiuGdujR4D6EJN9u2LWg/edit#gid=0)
which is a good reference on controller peripherals.

### Why C++?

C is a much more common programming language in the embedded space, so
our choice of C++ deserves some discussion.

Simply put, we chose C++ over C because we believe it is a more
productive programming language.  Here are some advantages we’ve found
to using C++.

-   In C we’d have to represent a pressure measurement as a number, e.g.
    a float.  This is
    [error-prone](https://mars.nasa.gov/msp98/news/mco990930.html) in
    part because the compiler can’t help you keep your units consistent.
    In contrast, our C++ code represents a pressure measurement using an
    explicit
    [Pressure](../common/libs/units/units.h) type.
    You can create a Pressure from a measurement in kPa or cmH2O and the
    software will do the unit conversions automatically. We also support
    operators between types.  For instance, dividing a Volume by a
    Duration yields an object of type VolumetricFlow, again with the
    units automatically correct. This is a zero-cost abstraction -- it
    runs just as fast as the equivalent C code -- and it eliminates
    whole classes of bugs.\
-   We use pieces of the C++17 standard library to add safety to our
    code.  For instance, we use C++’s std::variant class for
    discriminated unions instead of C’s union construct.  We also use
    std::optional throughout the code to represent a value that may not
    be present.  This is much safer than most C solutions (e.g. using a
    sentinel value like -1 or NaN to mean "not present").
-   Some language features of C++ are inherently safer than the
    respective features of plain C. For example, C++ requires the
    programmer to be explicit about type conversion in cases where the
    conversion may be lossy (e.g. from a floating-point to an integer
    type, or from an integer type to a more narrow integer type). In
    contrast, C allows such conversions implicitly, failing to protect
    against a common source of errors in safety-critical software.

We have configured our environment to disallow dynamic memory
allocation, and we do not use C++ exceptions.

### Software Provenance

We wrote all of the cycle controller software from scratch, with two
exceptions:

-   We use
    [nanopb](https://github.com/nanopb/nanopb) for
    protocol buffer encoding/decoding. Nanopb is an extensively tested
    library used in many projects, and protocol buffers are an industry
    standard for data exchange.
-   Our PID controller is based on an [Arduino
    library](https://github.com/br3ttb/Arduino-PID-Library/),
    although our version has evolved beyond the point of recognition --
    every line of code has been rewritten and our version is several
    times smaller by line count.  It has fewer features, and we have
    added extensive unit tests.

Notably, all of our code for interacting with the STM32 hardware is
bespoke; we are not using the Arduino STM32 hardware abstraction layer
or any other third-party HAL. This ensures auditability over every line
of code in this critical part of the system.

### Software Design

The cycle controller follows a modular design, described below.

Graph of components in cycle controller

The main loop runs every 10ms and has the following responsibilities:

-   Reset the watchdog timer. If the watchdog timer is not reset within
    250ms, the microcontroller assumes it is stuck and restarts.
-   Instruct comms to send a packet to GUI if necessary, and check
    whether comms has received a packet from the GUI.
-   Instruct controller to recalculate desired actuator positions, based
    on the commands in the latest packet received from the GUI.

Comms communicates with the GUI app running on the Raspberry Pi. Recall
that the communication protocol is simply that the controller
periodically sends all its state to the GUI, and the GUI periodically
sends all of its state to the controller, overwriting any previous
state. The protocol is defined
[here](../common/generated_libs/protocols/network_protocol.proto).

On each iteration of the main loop, the controller component forwards
the parameters from the GUI (e.g. PEEP 5, PIP 20, …) to the breath
FSM (finite state machine, see below), which responds with a "desired
system state", the physical properties we want the pneumatic system to
have at this moment. Since we have implemented pressure-controlled
ventilation modes, the main physical property to achieve is patient
pressure. The controller reads from the sensors, uses PID to calculate
the valve positions and fan power which it thinks will achieve the
desired state, and forwards these to the actuator.

The breath FSM (finite state machine) translates ventilator parameters
into a timeseries of desired states of the ventilator’s pneumatic
system. For example, the ventilator parameters "command pressure mode
with PEEP 5, PIP 20, RR 12 bpm, I:E 0.25" translates to the timeseries
"start pressure at 5 cmH2O, linearly ramping up to 20 cmH2O over 100ms;
sit at 20 cmH2O for 900ms; then drop to 5 cmH2O for 4s".

The breath FSM is also responsible for inspiratory effort detection in
pressure assist mode. In this case, the time series would keep pressure
at PEEP until either a breath is detected or it has been too long
between breaths.

The sensors module reads raw sensor voltages from HAL (hardware
abstraction layer, see below) and translates them into physical
measurements. It is responsible for calibrating the system’s three DP
sensors and translating the readings into two flow measurements (one for
each venturi) and one patient pressure measurement.

The actuators module receives a set of commands from the controller for
every actuator in the system, e.g. "blower speed 90%, inspiratory pinch
valve 28% open, etc.", and forwards them down to HAL to be acted upon.

The actuators module might seem like an unnecessary component -- why
can’t the controller simply call into HAL itself?  There are two
reasons.

-   Separating the choice of actuation state from actual actuation lets
    us unit test the controller.
-   When we run in simulation with Modelica for software-in-the-loop
    testing, we replace the real actuators component with a component
    that sends the commands to Modelica.

Finally, our HAL (hardware abstraction layer) is responsible for
communicating directly with the hardware, e.g. reading a voltage from
the STM32’s analog-to-digital converter. The HAL also sends commands to
the stepper drivers that control the ventilator’s pinch valves.

One last component which does not fit in the diagram or description
above is the debug module.  Among
other things, this powerful module lets us read and write values in the
controller without reflashing the device. We have used it to tune PID in
a live system, to operate the ventilator without the GUI attached (e.g.
for automated testing), and to capture and graph the ventilator’s
internal state as it runs.

### Algorithms of note

This section describes some significant algorithms implemented in the
cycle controller.

#### Valve control

The controller translates a desired patient pressure into
inspiratory/expiratory valve positions using closed-loop PID control.
The PID’s integral term is set based on the PEEP-to-PIP pressure delta
(i.e. some minor gain scheduling). The expiratory valve tracks the
inspiratory valve; as the inspiratory valve opens more, the expiratory
valve closes more.

#### Venturi pressure to flow conversion

We characterized the response of our venturis over a large range of
flows using a Fleisch pneumotachograph. We used a standard venturi
pressure-to-flow formula with a correction factor of 0.97 as the only
correction applied. The comparison between the two instruments matched
our empirical measurements very closely. The 0.97 correction factor is
in line with ISO recommendations for smooth surfaces with a Reynolds
number of \~104.

#### Volume zeroing

The net volume change over a breath is not always exactly 0, due to
leakage, sensor zero-point drift, and the fact that venturis have
relatively high error at low flows. A simple way to correct for this
would be to set volume at the beginning of every breath to 0, but this
introduces a discontinuity in the graph at each breath, which looks
wrong. And fundamentally it does not solve the problem; one can still
observe that volume measurements are "sloped".

Our volume zeroing algorithm addresses this. At the start of each
breath, we predict what the volume would be at the next breath if the
flow error remained constant. We then apply a flow offset to drive the
next breath’s volume to 0.

This works well on test lungs, but more work is required to characterize
its behavior in more realistic situations, like coughing, airway
blockage, etc. We also need to understand better users’ expectations
about how flow leakage should show up in the ventilator’s graphs. We
expect we will need a more sophisticated algorithm.

We track volume by integrating flow over time.  Getting an accurate flow measurement is challenging with our current
hardware, especially at low flow rates, where the venturi's SNR is worst.

We currently use a "big hammer" to address this, essentially forcing volume to 0 at each breath boundary.  This may hide
leaks and other clinically-relevant data from users, and so this algorithm likely needs to be improved in the future,
potentially in combination with different or additional sensors.

#### Inspiratory effort detection

We use the following algorithm to detect inspiratory effort in pressure
support mode.  First, we wait for flow to become nonnegative during the
exhale phase. Then we start keeping two [exponentially-weighted moving
averages](https://en.wikipedia.org/wiki/Moving_average%23Exponential_moving_average) of
flow. The "slow average" has a small alpha term and thus reacts slowly
to changes in flow. The "fast average" has a large alpha term and thus
reacts quickly. We can think of the slow average as characterizing
"normal flow" during the expiratory cycle (which we’ve observed on test
lungs does change, but slowly), while the fast average calculates
"current flow".  When the fast average exceeds the slow average by a
certain threshold, that triggers a breath.

This works well on our test lungs, but much more testing is needed to
see how it performs in more realistic situations. Graphs and a demo
video are available in
[02-1 Performance Evaluation](https://docs.google.com/document/d/1g7qLD5qD4BKfR1mcGq7-QY6XE2C9oIIw5GJdUzU31Zg/edit?ts%3D5eefc588%23heading%3Dh.pt7ef8fp4ywf).

### Status of Oxygen Flow Control

Our ventilator can currently deliver 100% oxygen (supplied by an external source of pressurized oxygen) or ambient air
(supplied via our blower fan), but cannot currently mix these two gasses.

Variable FiO2 requires a more complicated control scheme, controlling both the air proportional valve and the oxygen
proportional solenoid together. We are currently exploring two controller schemes for achieving this.  We've tried both
of these in the modelica model, though neither has been tried on hardware yet.

The first controller scheme is to ratio-control the two valves. In this scheme, a single PID commands both the air valve
and the oxygen valve simultaneously to achieve the desired pressure targets in the different breathe stages. The mapping
from the PID command to the actual valve command is determined by a ratio that is adjusted across breathe cycles by a
separate PID controller designed to achieve the desired FiO2.

The challenge with this scheme is that the current valves (the oxygen proportional solenoid and the air proportional
pinch valve) have extremely different response times, which may make it difficult to achieve stable control.

An alternative scheme is to use one of the valves to control pressure and the other valve to control FiO2. The valve
that is controlling pressure would be controlled by a PID during the inhale and exhale phases. The valve that is
controlling FiO2 would have a constant value across inhale and a constant value across exhale - these values would then
be adjusted by the FiO2 PID across breaths. For this scheme, if the FiO2 were below about 70-80%, then the air valve
would be used to control pressure and the oxygen valve would be used to manage FiO2; for higher FiO2, this would be
reversed.

The benefit of this approach is that it avoids trying to control both valves simultaneously. The downside of this
approach is that it can lead to greater FiO2 variability over a breath, has a greater risk of pressure over/undershoot,
and, for stability reasons, will likely necessitate a slower rate of FiO2 change. Based on discussions with doctors,
achieving the necessary FiO2 within 30-60s was deemed acceptable, meaning that a safer control scheme that minimizes
over/undershoot risk by adjusting FiO2 more slowly may be acceptable.

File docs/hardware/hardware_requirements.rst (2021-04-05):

.. hardware_requirements:

Hardware Requirements Specification
===================================

Purpose
-------

This document describe *what* |PROJECT_NAME| hardware must do.

This document is meant to be read and agreed-upon by the project owners and by software developers during design and construction.

.. todo:: Specify the functional requirements, performance requirements, interface requirements, safety requirements, hazard mitigations

Requirements
------------

Assembly
^^^^^^^^

.. item:: RW-HW-6
   :fulfills: RW-SYS-16

All subcomponents shall pass accelerated life testing equivalent to at least 336 hours (2 weeks continuous runtime)

.. item:: RW-HW-8
   :fulfills:

The construction, assembly, and maintenance of the device shall be compatible with metric tooling/set ups.

.. item:: RW-HW-10
   :fulfills: RW-SYS-16

The device must last 2000 hours if the maintenance schedule is followed.

.. item:: RW-HW-23
   :fulfills:

The ventilator shall be operable by a user wearing standard PPE (e.g. latex or nitrile gloves)

.. item:: RW-HW-30
   :fulfills: RW-SYS-63 RW-SYS-77

The patient circuit shall interface with the vent thru 22mm ID tubing.The patient circuit shall interface with nasal cannulas or pillows through a standard 15mm ET tube adapter interface.

.. item:: RW-HW-33
   :fulfills: RW-SYS-12

The assembly shall feature HEPA filters on the blower intake and exhaust pathways

.. item:: RW-HW-43
   :fulfills: RW-SYS-124

Enclosure openings shall not exceed 12.5mm diameter and shall feature no openings on the top face .

.. item:: RW-HW-44
   :fulfills: RW-SYS-124

Ventilation openings on the enclosure shall not be adjacent to electronics or other sensitive components targeted by IEC 61000-4-1 series of test.

.. item:: RW-HW-45
   :fulfills: RW-SYS-137

All hardware components shall operate without adverse effect at altitudes up to 10000 ft.

.. item:: RW-HW-46
   :fulfills: RW-SYS-140

Enclosure does not degrade when cleaned with X% bleach solution

.. item:: RW-HW-47
   :fulfills: RW-SYS-136

Gas inlet ports are clearly labeled per X

Pneumatics
^^^^^^^^^^

.. item:: RW-HW-3
   :fulfills: RW-SYS-92

The blower shall provide a flow rate of at least 60 L/min.(Stretch goal) the blower shall provide a flow rate of at least 130 L/min.

.. item:: RW-HW-11
   :fulfills: RW-SYS-10

The overpressure relief device shall be set to automatically relieve pressure at or above 60 cm H2O.

.. item:: RW-HW-12
   :fulfills: RW-SYS-144 RW-SYS-92

The device must not let the patient asphyxiate if they are attempting to breathe, even if the device fails. This can be achieved by preventing pressure from dropping below -4 cm H20 and limiting the resistance to 3 cmH20/l/s

.. item:: RW-HW-15
   :fulfills: RW-SYS-42

The pneumatic circuit shall reach maximum flow rate (e.g. 60 L/min) in 100 ms.

.. item:: RW-HW-16
   :fulfills: RW-SYS-89

The device must be able to detect that a patient is trying to trigger an inhale or exhale. This requires being able to measure changes in flow rate to a resolution of 5 L/min during inspiratory and expiratory holds.

.. item:: RW-HW-35
   :fulfills: RW-SYS-76 RW-SYS-24

The oxygen input port shall be DISS compatible up to 440 kPa

Electronics
^^^^^^^^^^^

.. item:: RW-HW-27
   :fulfills: RW-SYS-121 RW-SYS-119 RW-SYS-120

The device shall provide a battery monitor for assessing battery presence, charge, and failure.

.. item:: RW-HW-28
   :fulfills: RW-SYS-121 RW-SYS-120 RW-SYS-119 RW-SYS-117 RW-SYS-118

The device shall provide a sensor indicating whether power is coming from AC or battery and whether AC is available

.. item:: RW-HW-32
   :fulfills: RW-SYS-103 RW-SYS-102 RW-SYS-101 RW-SYS-32 RW-SYS-5 RW-SYS-3

The display shall support touch input, 8-bit color and a minimum refresh rate of 30 fps.

.. item:: RW-HW-34
   :fulfills: RW-SYS-16

The electronic non-volatile memory shall be rated for at least 10e6 read/write cycles.

.. item:: RW-HW-36
   :fulfills: RW-SYS-74 RW-SYS-117 RW-SYS-50

The device battery shall have a charge capacity of X Ah at 12 volts nominal.

.. item:: RW-HW-38
   :fulfills: RW-SYS-69

The electronics shall include a real-time clock with independent battery (e.g. coin cell) supply.

.. item:: RW-HW-39
   :fulfills: RW-SYS-69

The electronics shall include non-volatile memory of at least 1GB

Sensors and Actuators
^^^^^^^^^^^^^^^^^^^^^

.. item:: RW-HW-2
   :fulfills: RW-SYS-111 RW-SYS-110 RW-SYS-115 RW-SYS-3 RW-SYS-5

The pressure sensor shall have a resolution of 1 cmH2O and a range of 0 - 60 cmH2O

.. item:: RW-HW-4
   :fulfills: RW-SYS-113 RW-SYS-112 RW-SYS-116 RW-SYS-115 RW-SYS-89 RW-SYS-32

The inhale and exhale flow sensors shall have a resolution of X L/min and a range of Y L/min.

.. item:: RW-HW-21
   :fulfills: RW-SYS-72

The O2 sensor shall measure oxygen fraction from 21% to 100% with an accuracy of 5%.

.. item:: RW-HW-41
   :fulfills: RW-SYS-122

The temperature sensors shall have range -40 to +125 C with a minimum resolution of 1 C

Traceability Matrix
===================
.. item-matrix:: System Requirements to Hardware Requirements
   :target: RW-SYS-
   :source: RW-HW-
   :sourcetitle: Hardware Requirements
   :targettitle: System Requirements
   :type: fulfills

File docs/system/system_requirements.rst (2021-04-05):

.. system_requirements:

System Requirements
===================

This document defines the system requirements for |PROJECT_NAME|.

Assembly
^^^^^^^^

.. item:: RW-SYS-12
   :fulfills: SR-17

The device shall filter intake and exhaust to below 0.3 um (HEPA) or finer in order to limit the spread of virus from contaminated patients and to prevent the contamination of the device from patients.

.. item:: RW-SYS-16
   :fulfills: SR-28

The device must be able to work continuously (100% duty cycle) for a minimum of 48 hours and a target of 2 weeks without pause for maintenance, downtime, or repair.The device must operate after 2000 hours of storage time.

.. item:: RW-SYS-54
   :fulfills: SR-15

The system components that come into contact with the patient airway circuit shall be compatible with ISO 18562-1 thru ISO 18562-4.

.. item:: RW-SYS-63
   :fulfills: SR-29

The device shall be have the ability to integrate a hot water humidifier, the humidifiers that meet ISO 80601-2-74:2017 are compatible with 22mm Respiratory Tubing per ISO 5356 standard. (Note that the fitting for standard breathing tubes and humidifiers is the same)

.. item:: RW-SYS-124
   :fulfills:

Ventilator shall have ingress protection level of IP21.IP2x = No penetration into ventilator by solid objects > 12.5mm (e.g. fingers)IPx1 = Dripping water (vertically falling drops) shall have no harmful effect.Ref: www.dsmt.com/resources/ip-rating-chart/

.. item:: RW-SYS-136
   :fulfills: SR-34

Gas inlet shall be clearly labelled with gas type, color, and specified pressure ranges along with direction of flow

.. item:: RW-SYS-137
   :fulfills: SR-27

Ventilator shall operate at altitudes below 10k ft

.. item:: RW-SYS-140
   :fulfills: SR-18

The ventilator construction shall continue to operate while being disinfected by standard cleaning agents (e.g. bleach solution of X%)

.. item:: RW-SYS-141
   :fulfills: SR-16

The ventilator design shall include antiviral filters on the patient inhale and exhale limbs.

.. item:: RW-SYS-144
   :fulfills:

Patient shall to be protected against both asphyxiation and barotrauma in the event of a power, mechanical, or computing failure.

.. item:: RW-SYS-150
   :fulfills:

The hardware shall not compromise basic safety and essential performance while stress tested per IEC 60068-2-78 (damp heat).

.. item:: RW-SYS-155
   :fulfills: SR-33

The device, when fully assembled and tested against IEC 60601-1 section 9.6.2, shall not exceed 80 dBa. Test specifications in 80601-2-12 201.9

.. item:: RW-SYS-156
   :fulfills: SR-30

The assembly shall conform to transit-operable (80601-2-12 201.15.3.5.101.2) shock tests per IEC 60068-2-27:5g for 6ms, half-sine, 3x per axis

.. item:: RW-SYS-157
   :fulfills: SR-30

The assembly shall conform to transit-operable (80601-2-12 201.15.3.5.101.2) vibration tests per IEC 60068-2-24. Basic safety and essential performance shall not be compromised during or after this test.10 Hz - 100 Hz: 0.33 (m/s2)2/Hz, 30 min per axis100 Hz - 500 Hz: 6 dB per octave, 30 min per axis

.. item:: RW-SYS-158
   :fulfills: SR-30

The assembly shall conform to transit-operable (80601-2-12 201.15.3.5.101.2) drop tests per IEC 60068-2-31. Basic safety and essential performance shall not be compromised during or after this test.10 cm vertical drop, twice per specified attitude (TBD)NOTE: as of writing it is assumed the ventilator shall weigh between 1-10 kg

Pneumatics
^^^^^^^^^^

.. item:: RW-SYS-9
   :fulfills:

The device shall prevent pressure from dropping below -4 cm H20 and limit the resistance to 3 cmH20/l/s.

.. item:: RW-SYS-10
   :fulfills: SR-20

The device must, through inherently safe features, prevent patient pressures from exceeding 60 cmH2O in any operating cases or failure modes.

.. item:: RW-SYS-24
   :fulfills: SR-12

The device shall be compatible with oxygen (DISS) up to 440 kPa

.. item:: RW-SYS-92
   :fulfills: SR-7

The device shall be capable of a peak inspiratory flow rate of at least 60L/min for at least 30 seconds.NB This supports a minute volume of at least 30 L.

.. item:: RW-SYS-148
   :fulfills:

The pneumatic circuit shall not leak more than 1-2 L/min at 60 cmH2O

Electronics
^^^^^^^^^^^

.. item:: RW-SYS-50
   :fulfills: SR-35

The device battery shall be sized to provide 1 hour of operation at 12 volts nominal.

.. item:: RW-SYS-57
   :fulfills:

The system shall be compatible with 110V/60Hz and 220V/50HZ AC mains.
RW-SYS-069,The ventilator shall provide non-volatile data storage of at least 1GB.,,HW-039

.. item:: RW-SYS-69
   :fulfills:

The ventilator shall provide non-volatile data storage of at least 1GB.

.. item:: RW-SYS-74
   :fulfills:

The ventilator shall be capable of being run from a 12V power supply

.. item:: RW-SYS-149
   :fulfills: SR-24

The device must detect through physical means the disconnection of the oxygen supply from the o2 input line.

.. item:: RW-SYS-153
   :fulfills: SR-33

The 12 volt power supply shall be compatible or certified against IEC 60601-1

.. item:: RW-SYS-154
   :fulfills: SR-22

The hardware shall feature specific sensors for detecting tube dis/connection

.. item:: RW-SYS-159
   :fulfills:

The ventilator shall provide a Real Time Clock for timestamping all event log data

HMI
^^^

.. item:: RW-SYS-3
   :fulfills: SR-26 SR-4

The system shall control the target peak inspiratory pressure (PIP) from 5-55 cmH2O in increments of 1 cm H2O.The system shall measure and numerically display patient pressure in the range of 0 - 60 cmH2O with resolution 1 cmH2O.The system shall display the measured pressure as a graph with duration of 30 seconds updated at a rate >= 20Hz and units of cmH2O.

.. item:: RW-SYS-5
   :fulfills: SR-26 SR-8

The system shall control the target PEEP from 0 - 20 cm H2O in increments of 1 cmH2O.The system shall measure and numerically display the PEEP in the range of 0 - 20 cmH2O in increments of 1 cmH2O.

.. item:: RW-SYS-20
   :fulfills: SR-26 SR-10

The system shall control the respiratory rate (RR) from 5-30 breaths per minute (bpm) in increments of 1 bpm.The system shall measure and numerically display RR in the range of 0 - 30 bpm with resolution 1 bpm.

.. item:: RW-SYS-21
   :fulfills: SR-9

The device shall control the time ratio of inspiration and expiration (I:E ratio) from 1:1 to 1:4 (Inhale to exhale). Increments of 1: 0.1The system shall measure and numerically display I:E ratio in the range of 1:1 to 1:4 with resolution 1:0.1.

.. item:: RW-SYS-32
   :fulfills: SR-26 SR-11

The system shall control inspiratory tidal volumes ranging from 200-800ml with increments of 10mLThe system shall measure and numerically display the inspired tidal volume in range of 0 - 1000 mL with resolution of 10mLThe system shall display the inspired tidal volume as a graph with duration of 30 seconds updated at a rate >= 20Hz and units of mL.

.. item:: RW-SYS-72
   :fulfills: SR-13

The device shall control the fraction of inspired O2 (FiO2) in supplied air from 0.21 to as close to 1 as possible with a minimum of 0.9, adjustable in increments of 0.05.The system shall measure and numerically display the patient FiO2 in range of 21-100% with resolution of 1%.

.. item:: RW-SYS-87
   :fulfills: SR-26

The system shall display the flow rate provided to the patient as a graph with duration of 30 seconds updated at a rate >= 20Hz and units of liters / minute.

.. item:: RW-SYS-143
   :fulfills: SR-11

Ventilator shall support user entry of patient gender and height. This data shall be used to calculate ideal body weight (IBW).Ventilator shall support the display of tidal volumes as both volume (units mL) and volume per kg IBW (units mL/kg or cc/kg)

.. item:: RW-SYS-147
   :fulfills:

The system shall display pressure/volume loops.

Manager
^^^^^^^

.. item:: RW-SYS-77
   :fulfills:

The system shall support a HFNC operational mode. In this mode there are no breath cycles. The operator defines the following control parameters:constant flow rate (up to maximum possible L/min)constant FiO2 (21-100%).Display parameters: Patient pressure (cmH2O), flow rate (L/min), FiO2 %Relevant alarms: Low/high FiO2 triggers, Low/high pressures

.. item:: RW-SYS-131
   :fulfills:

The ventilator shall have a pre-test mode where the patient inhalation port and patient exhalation port are connected and the operation of the device is checked including the capability to produce the correct pressure and flow rate, the function of valves, and the function of tidal volume measurement.

.. item:: RW-SYS-132
   :fulfills: SR-6 SR-4 SR-2 SR-1

The system shall support Pressure Assist Mode. In this mode a breath cycle is defined by the control parameters below. The patient can exceed the respiratory rate by initiating additional breaths, but the breath parameters do not change.Control parameters:PIP. Peak Inspiratory Pressure.PEEP. Positive End-Exhalatory Pressure.FiO2. Fraction of Inspired Oxygen.I-time. Inspiratory (rise + dwell) time.Inspiratory sensitivity.RR. Respiratory Rate.Display parameters: PIP/PEEP/RR/FiO2/I:E ratio/tidal volume.Relevant Alarms: * Low tidal volume * High tidal volume * High RR

.. item:: RW-SYS-133
   :fulfills: SR-5

The system shall support Pressure Support Mode. In this mode the breath cycle shall be defined by the control parameters below. The breath cycle shall be triggered exclusively by the patient.Control parameters:SIP: Support Inspiratory Pressure. Like PIP, but specified as a support pressure, not a target pressure.PEEP. Positive End-Exhalatory Pressure.FiO2. Fraction of Inspired Oxygen.I-time. Inspiratory (rise + dwell) time.Inspiratory sensitivity (change in flow rate at PEEP)Expiratory sensitivity (change in flow rate at P_plateau)Display parameters: PIP/PEEP/RR/FiO2/I:E ratio/tidal volume.Relevant Alarms: * Low tidal volume * High tidal volume * Low RR (apnea) *

.. item:: RW-SYS-134
   :fulfills:

The system shall support Pressure Control Mode. This mode shall not be featured. It is effectively a subset of Pressure Assist with zero patient inspiratory effort.

.. item:: RW-SYS-146
   :fulfills: SR-3

The system shall support Volume Assist mode. In this mode a breath cycle is defined by the control parameters below. The patient can exceed the respiratory rate by initiating additional breaths, but the breath parameters do not change.Control parameters:VT. Tidal volume.PEEP. Positive End-Exhalatory Pressure.FiO2. Fraction of Inspired Oxygen.I-time. Inspiratory (rise + dwell) time.Inspiratory sensitivity.Expiratory sensitivity.RR. Respiratory Rate.Display parameters: PIP/PEEP/RR/FiO2/I:E ratio/tidal volume.Relevant Alarms: * Low pressure * High pressure * High RR

.. item:: RW-SYS-160
   :fulfills:

The manager shall log at least 5000 events in an event log, including at least the following items:- Ventilation starts and stops- All confirmed Ventilation settings- All confirmed alarm settings- All occurrences and ends of alarms with all their related actions: Inhibitions, cancellations, resets, acknowledge button presses.

.. item:: RW-SYS-161
   :fulfills: SR-11

Measurement of tidal volume must be accurate to within 10mL

.. item:: RW-SYS-163
   :fulfills: SR-20

GUI must compute PIP over each breath

.. item:: RW-SYS-164
   :fulfills: SR-10

GUI must compute the breath rate based on controller sensor readings

.. item:: RW-SYS-165
   :fulfills: SR-9

Algs must be able to detect inspiration and expiration phase and how long it took.

.. item:: RW-SYS-167
   :fulfills: SR-30

GUI needs to automatically invoke a safety action when blower motor temperature is above threshold

.. item:: RW-SYS-168
   :fulfills:

GUI should be able to compute the rise time for each breath

.. item:: RW-SYS-169
   :fulfills:

Controller must keep track of #cycles of wear of various components and issue alarms if they're nearing their lifespan

Controller
^^^^^^^^^^

.. item:: RW-SYS-42
   :fulfills:

The device shall reach the commanded patient pressure within 100 ms of detecting respiratory effort.

.. item:: RW-SYS-89
   :fulfills: SR-5

The minimum detectable inspiratory effort shall be 5 L/min.

.. item:: RW-SYS-94
   :fulfills: SR-20

The pressure overshoot during the pressure fall phase shall not exceed 0.8*PEEP-1 cmH2O

.. item:: RW-SYS-95
   :fulfills: SR-20

The pressure overshoot during the pressure rise phase shall not exceed 2 cmH2O.

.. item:: RW-SYS-142
   :fulfills: SR-31

The device shall ensure control parameters are within 10% of commanded values in each of the test conditions specified in 80601-2-12 table 201.104.

.. item:: RW-SYS-152
   :fulfills:

The device needs to be able to achieve the FiO2 target within 30-60s

.. item:: RW-SYS-162
   :fulfills:

Controller must detect onset of respiratory effort within X ms

.. item:: RW-SYS-166
   :fulfills:

Controller shall report to the Manager the moments when each breath begins (patient-triggered or automatic)

Alarms
^^^^^^

.. item:: RW-SYS-17
   :fulfills: SR-25

The device parameters and alarms shall be readable at a distance of 1 meter.The device alarms shall be audible (60-80 dBa) at a distance of 1m

.. item:: RW-SYS-68
   :fulfills:

The device shall be allow the user to view all alarms if multiple alarms are simultaneously present.

.. item:: RW-SYS-98
   :fulfills:

The system shall have multiple priority alarms indicating the severity of the condition. These modes shall be:High - Likely to cause PATIENT injury or death within seconds to several minutes if uncorrectedMedium - Do not cause PATIENT injury or death until at least several to many minutes have elapsedLow - May cause PATIENT injury only after many minutes to hours have passed

.. item:: RW-SYS-101
   :fulfills:

High severity visual alarms shall be indicated with a red color and a flashing frequency of 1.4-2.8 Hz with a 20-60% duty cycle.High severity audio alarms shall have the following characteristics defined by 60601-1-8:an auditory burst of 10 pulsespulse tone frequency shall be 150-1000Hz.There shall be at least 4 harmonic components of the pulse tone in the range 300-4000 Hz.The effective pulse duration shall be 75-200 ms.See attached table for burst description.

.. item:: RW-SYS-102
   :fulfills:

Low severity alarms shall be indicated with a cyan or yellow color which shall be constantly on.

.. item:: RW-SYS-103
   :fulfills:

Medium severity alarms shall be visually indicated with a yellow color, and a flashing frequency of 0.4-0.8Hz with a 20-60% duty cycleMedium severity alarms shall have the following characteristics defined by 60601-1-8:pulse tone frequency shall be 150-1000Hz.There shall be at least 4 harmonic components of the pulse tone in the range 300-4000 Hz.The effective pulse duration shall be 125-250 ms.See attached table for burst description.

.. item:: RW-SYS-106
   :fulfills:

A press on the AUDIO PAUSE / ALARM PAUSE key shall initiate an auditory alarm signal pause of all active alarms up to 120 seconds. The alarm activation symbol shall be displayed during the inactivation state with the symbol IEC 60417-5576

.. item:: RW-SYS-107
   :fulfills:

The system shall have a means to dismiss alarms which have been previously triggered.

.. item:: RW-SYS-110
   :fulfills: SR-22

The operator can set a threshold for a low patient pressure alarm in the following ranges:Low Patient Pressure alarm: 0-20 cmH2O, 1 cmH2O incrementsWhen the alarm thresholds are triggered the system shall initiate a high priority alarm.

.. item:: RW-SYS-111
   :fulfills: SR-20

The operator can set a threshold for a high patient pressure alarm in the following ranges:High Patient Pressure alarm: 20-60 cmH2O, 1 cmH2O increments. Default: PIP+5 cmH2OThis alarm shall trigger if the patient pressure exceeds the set PIP for three consecutive breath cycles.The audible indicator shall silence upon the first breath that goes below the threshold, but the visual indicator shall remain active until the alarm is cleared.

.. item:: RW-SYS-112
   :fulfills: SR-23

The operator can set thresholds for low and high exhaled tidal volume (VTE) alarms in the following ranges:High VTE alarm: 500-3000 mL, 10 mL incrementsLow VTE alarm: 0-1000 mL, 10 mL incrementsWhen the alarm thresholds are triggered the system shall initiate a medium priority alarm.This alarm does not apply in HFNC mode.

.. item:: RW-SYS-113
   :fulfills: SR-23

The operator can set thresholds for low and high inspired tidal volume (VTI) alarms in the following ranges:High VTI alarm: 500-3000 mL, 10 mL incrementsLow VTI alarm: 0-1000 mL, 10 mL incrementsWhen the alarm thresholds are triggered the system shall initiate a medium priority alarm.This alarm does not apply in HFNC mode.

.. item:: RW-SYS-114
   :fulfills: SR-22

The ventilator shall initiate a high priority alarm when the proximal tube is not connected for all ventilation modes.

.. item:: RW-SYS-115
   :fulfills: SR-23

The ventilator shall initiate a high priority alarm if no significant volume can be delivered to the patient while the target pressure is reached (e.g. patient circuit blockage detected).

.. item:: RW-SYS-116
   :fulfills:

The operator can set a maximum leak threshold as follows:* Leak threshold: 5-60 L/min, 1 L/min incrementsA high priority alarm shall be triggered when leakage above this threshold is observed in the patient circuit.

.. item:: RW-SYS-117
   :fulfills:

The ventilator shall initiate continuous tone alarm when shut down occurs while ventilating. The alarm shall last at least 2 min.

.. item:: RW-SYS-118
   :fulfills: SR-19

The ventilator shall provide a low priority alarm if an AC power source (previously available) is lost or disconnected

.. item:: RW-SYS-119
   :fulfills: SR-19

A ventilator operating on battery shall provide a medium priority alarm when the estimated remaining operating time is 30 minutes or below.

.. item:: RW-SYS-120
   :fulfills: SR-19

A ventilator operating on battery shall provide a high priority alarm when the estimated remaining operating time is 10 minutes or below.

.. item:: RW-SYS-121
   :fulfills:

The ventilator shall provide a high priority alarm if the battery is absent or not available, or if the battery is unchargeable.

.. item:: RW-SYS-122
   :fulfills:

Temperatures of critical system elements shall be monitored. A high priority alarm shall trigger if these elements exceed their recommended temperatures.BlowerElectronicsBatteryTBD: Do we cut back on ventilation as a fallback (preserve the ventilator at risk to patient)

.. item:: RW-SYS-128
   :fulfills: SR-6 SR-21

The operator can set thresholds for low and high respiratory rate (RR) alarms in the following ranges:High RR alarm: 5-30 bpm, 1 bpm incrementsLow RR alarm: 2-30 bpm, 1 bpm incrementsWhen the alarm thresholds are triggered the system shall initiate a medium priority alarm.This alarm does not apply in HFNC mode.

.. item:: RW-SYS-139
   :fulfills: SR-24

The ventilator shall issue a high priority alarm in the event of O2 disconnection

.. item:: RW-SYS-151
   :fulfills: SR-25

The device shall provide an audible alarm system that can:provide volume at 60 dBa from 150 Hz to 4000 Hzproduce volume from an electrical signal within 33 ms

Traceability Matrix
===================
.. item-matrix:: System Requirements to SRS
   :source: RW-SYS
   :target: RW-SW
   :targettitle: Software Requirements
   :sourcetitle: System Requirements
   :type: fulfilled_by

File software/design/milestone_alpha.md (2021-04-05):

# This milestone is complete.

_Information below only for posterity._

# Objectives
* Provide a physical proof-of-concept for demonstration and review with medical experts
  * See **Demo script** section below.

* Provide a platform for continuous engineering experimentation
  * E.g. Edwin will want to play with the thing with a test lung. Ideally the software should be conductive to that, e.g. have the parameters adjustable via UI rather than baked in.

# Requirements

* Must have a minimal GUI (graphical user interface) that can display pressure trace, flow trace, volume trace
  * GUI is ideally our specialized QT GUI, but if that's not ready by demo time, we can use [DEPRECATED LINK].
    * *jlebar*: That approach won't work with our current protobuf-based protocol.  We can change our code to output something parseable by that tool if necessary, but my preference would be to do something that we don't have to throw away.  For example, Albertas put together a [proof of concept Python script](https://github.com/RespiraWorks/Ventilator/commit/330895ea391ee70cf156fb5bd8673434b3908846) that reads protobuf data from the Arduino.  We could use an approach like this to draw graphs in Python.

* GUI must obtain pressure, flow, volume data from the controller
  * [Per Ethan](https://respiraworks.slack.com/archives/C012H3G1GQ5/p1587857837002500): Flow/volume do not need to be right, just look right:
  * Ideally, use sensor readings with calibration at device startup and smoothing
  * But for alpha, OK to do calibration once on the demo device and hard-code calibration parameters; omit smoothing
  * Absolute worst case, use synthetic data for demo

* Controller must implement Pressure Control (aka Command Pressure) mode
  * Defined in [this presentation slide](https://docs.google.com/presentation/d/1DA1BQlCj8wNv60pGGzrldPfZBmr6WAH4WbrD4W7i43U/edit#slide=id.g739b1a32cc_0_12), prototyped in [pid.cpp](https://github.com/RespiraWorks/Ventilator/blob/fee155d5d4e8fa029b2e83e4753cfaeb15b9b365/controller/src/pid.cpp), correct implementation tracked [here](https://github.com/RespiraWorks/Ventilator/issues/17)
  * Within alpha, for demo, controller can implement this autonomously, i.e. with parameters hard-coded in the controller rather than obtained from the GUI.
  * However, getting mode parameters from GUI is a nice-to-have, per objective 2 above.

* Must not crash irrecoverably or self-destruct.

# Demo Script
This is a narrative description of how we expect the alpha test to go.  We will probably be running a subset of the tests described in Appendix B of the [MHRA Requirements](https://assets.publishing.service.gov.uk/government/uploads/system/uploads/attachment_data/file/879382/RMVS001_v4.pdf).

* Hook up RespiraWorks Ventilator to a test lung
* Turn on device and begin showing data on a screen, either on the GUI or a laptop
* Run a set of respiratory cycles at default, middle of the range values.
* Adjust each of PIP, PEEP, I:E, and RR one at a time, starting from default values, while recording data.
* Run some of the more extreme corner cases involving two or more of the above settings (i.e. High PIP, low PEEP, Low I:E, high RR, high resistance on test lung, high compliance on test lung), while recording data.
* Simulate common failure modes (leaky loop, patient obstruction, etc), while recording data.
* Simulate patient inspiratory effort, record data.
* End test

*TODO(2020-04-29)* Clarify with Edwin: What behavior do we expect SW to have in extreme cases / failure modes?  Similarly, what behavior do we expect when simulating patient effort?  Current understanding is that, nothing is needed from software.

* Note: For patient effort, failure modes, and corner cases, we don't except the alpha software to do anything except continue to drive the respiration cycle according to the set parameters.  We just want to record what these cases look like to our sensors.

# Excluded

The alpha milestone is part of the project's overall [requirements](https://respiraworks.github.io/Ventilator/software/SRS.html). Anything mentioned there but not here, is excluded from alpha.

If you have further questions, ask on [#alpha-reqs](https://app.slack.com/client/T0102KRCH5M/C012H3G1GQ5/thread/C0100SF3N5T-1587858521.093800).

# Issue hotlists

Proceed with caution: these need cleanup.

- Controller: https://github.com/RespiraWorks/Ventilator/milestone/4
- GUI: https://github.com/RespiraWorks/Ventilator/milestone/1

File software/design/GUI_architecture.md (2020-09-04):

## User Interface (UI) Controller

The UI controller runs on a Raspberry Pi with a touchscreen and is
written in C++17 using QT as the user interface framework. The reasoning
behind this technology choice is described above, in the "Software
Design" section. Below we discuss the GUI features and architecture in
more detail.

There is a page on [User interface requirements](UI_requirements.md).

### Features

The most important features of the UI are displaying data and adjusting
ventilation parameters.

-   Data Display: The UI controller presents the user with the data
    coming from the ventilator, including both the actual sensor data
    and values that are derived from it (e.g. tidal volume and PIP/PEEP
    of the most recent breath). The data presented includes the standard
    respiratory cycle plot that most doctors and technicians would
    expect.
-   User Mode / Parameter Setting and Adjustment: The UI controller
    allows the user to set the desired ventilator mode and the desired
    control settings for that mode. The two modes currently supported
    are Pressure Control and Pressure Assist, as they are the modes
    supported by the Cycle Controller. The settings and ventilation mode
    can be changed at any time during operation, and adjusting a setting
    requires confirmation.
-   System state display: The UI controller displays a power source /
    battery status indicator and current time. Currently the battery
    status indicator uses a hard-coded value because the physical design
    lacks sensors to provide that data.

The UI implements an alarm subsystem based on ISO-60601-1-8.

-   Alarm State Detection: The UI controller is responsible for alarming
    when off-nominal events occur that require a clinician’s attention.
    The currently implemented alarms include over/under pressure (PIP is
    overshot or undershot by a certain amount compared to the commanded
    value) and disconnection of the patient circuit. The alarm
    architecture is robust and extensible, allowing us to easily add
    other alarms in the future.
-   Alarm Alerting and Information Display: The UI controller alerts the
    user to alarms through visual and audio cues:

-   Whenever an alarm condition is active, relevant sections in the UI
    are highlighted with color corresponding to the alarm priority. For
    example, over/under pressure alarms highlight the pressure graph.
-   If an alarm condition has been triggered, the UI emits an audio
    signal compliant with ISO 60601-1-8 according to the alarm priority
    until the alarm is acknowledged. If there are multiple
    unacknowledged alarms, the audio is based on the highest-priority
    one.
-   In ISO terminology, the audio signal is "latching": it persists even
    if the alarm condition is no longer active, so that the operator is
    made aware of a prior hazardous condition even if the condition
    activates sporadically and disappears before the operator walks up
    to the device upon hearing the audio signal.

-   Alarm Lifecycle: Whenever there are any unacknowledged alarms, the
    UI displays a banner showing the highest-priority currently
    unacknowledged alarm and offering to pause this alarm’s audio signal
    for 2 minutes.
-   Silenced alarms: The UI has a widget displaying the number of
    currently active but silenced (acknowledged) alarms, the highest
    priority of the alarms, and a countdown until the highest-priority
    alarm is unpaused.
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

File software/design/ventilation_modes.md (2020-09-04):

# Ventilation modes

This list is probably not complete. **Please improve.**
**TODO:** link to requirements

## PS, SIMV and PRVC Ventilator Modes

Currently, the ventilator has a CMV mode, where the device provides commanded breaths at a set rate and with a
controlled pressure profile, and a pressure assist mode, where the device triggers breaths by detecting inspiratory
effort.

The next modes planned to be added are pressure support (PS), Synchronized intermittent mandatory ventilation (SIMV),
and pressure regulated volume control (PRVC).

Pressure support is the most developed mode. Currently, the system is implemented in our Modelica simulation
environment, and our pressure assist mode gives us experience detecting patient effort. SIMV and PRVC were originally
higher priority modes, but after extensive consultation we determined that most doctors would be most comfortable for
most patients using CMV and AC/P, and so we focused on improving those modes first as much as possible.
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

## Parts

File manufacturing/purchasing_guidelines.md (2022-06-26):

# Part Purchasing Guidelines

**DEPRECATED - this page is deprecated, as it is being migrated to Sphinx-generated documentation. Please read the new Purchasing Guidelines [here](https://respiraworks.github.io/Ventilator/purchasing/index.html)**

> TODO: delete this page once all BOMs are migrated to Sphinx

## Purchasing Source Key

For older assemblies that you may still browse within the repository, you may find the following useful.

Items listed in the sub-assembly pages throughout this repo use the following abbreviations to identify the various suppliers.

* **Rw** = Built by RespiraWorks / DIY
* **A** = Ali Express
* **C** = McMaster-Carr
* **Cs** = Cables & Sensors
* **F** = Fast Eddy Bearings
* **G** = Grainger
* **Gn** = Generant
* **K** = Digikey
* **M** = Mouser
* **O** = Monoprice
* **R** = RS computing
(**note**: links provided are for worldwide customers; there are local RS retail sites for most countries that use the
same product reference (RS Stock No.) and will probably ship faster if you order from your country's site)
* **S** = ST
* **Sm** = SMC Pneumatics
* **T** = Stepperonline.com
* **U** = Uflow
* **W** = Wonsmart
* **Z** = Amazon

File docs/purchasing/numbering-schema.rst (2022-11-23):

Parts numbering schema
----------------------

The RespiraWorks parts numbering schema is designed with interdisciplinary maintenance of documentation in mind. Because of this, part numbers must be:

* semantically intuitive - reading the number should give you a rough idea of what this part is
* unambiguous - should be easy to disambiguate similar parts

Currently proposed (incomplete) schema is as follows::

    CS-descriptor[-nn]

**Mandatory sections:**

* CS - Category + Subcategory
    * e - electrical
        * ee - electronics, computing
        * ep - power - batteries, external adapters, etc..
        * ew - wiring
        * ec - connectors
    * p - pneumatics
        * pa - active valves - solenoids, etc..
        * pp - passive valves - one-way, overpressure
        * pf - fittings and tubing adapters
        * pt - tubing
    * m - mechanical
        * mm - metal, sheet metal, etc..
        * mp - plastics, acrylic sheets, etc..
        * mh - hardware
    * c - cosmetic
        * cs - stickers, safety labels
    * t - tools
        * te - tools, electrical
        * tm - tools, mechanical
        * tp - tools, pneumatic
        * tc - tools, cosmetic
* descriptor - short alphanumeric descriptor, preferably around 4-5 characters long

**Optional section:**

The *nn* is some numeric suffix that may be added to disambiguate a part that would otherwise have the same code to the left of it.

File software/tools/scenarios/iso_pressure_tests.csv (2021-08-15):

id | lung_compliance | lung_resistance | forced_breath_rate | forced_ie_ratio | forced_pip | forced_peep | forced_fio2 | forced_mode | expected_tv | description
iso_pc_1 | 50 | 5 | 20 | 0.5 | 15 | 5 | 30 | pressure_control | 500 | ISO 80601 pressure control test scenario 201.105.1
iso_pc_2 | 50 | 20 | 12 | 0.25 | 25 | 10 | 90 | pressure_control | 500 | ISO 80601 pressure control test scenario 201.105.2
iso_pc_3 | 20 | 5 | 20 | 0.5 | 30 | 5 | 90 | pressure_control | 500 | ISO 80601 pressure control test scenario 201.105.3
iso_pc_4 | 20 | 20 | 20 | 0.5 | 35 | 10 | 30 | pressure_control | 500 | ISO 80601 pressure control test scenario 201.105.4
iso_pc_5 | 20 | 20 | 20 | 0.5 | 20 | 5 | 30 | pressure_control | 300 | ISO 80601 pressure control test scenario 201.105.5
iso_pc_6 | 20 | 50 | 12 | 0.25 | 35 | 10 | 90 | pressure_control | 300 | ISO 80601 pressure control test scenario 201.105.6
iso_pc_7 | 10 | 50 | 20 | 0.5 | 35 | 5 | 90 | pressure_control | 300 | ISO 80601 pressure control test scenario 201.105.7
iso_pc_8 | 10 | 10 | 20 | 0.5 | 35 | 10 | 30 | pressure_control | 200 | ISO 80601 pressure control test scenario 201.105.8
iso_pc_9 | 3 | 10 | 30 | 0.429 | 20 | 5 | 30 | pressure_control | 50 | ISO 80601 pressure control test scenario 201.105.9
iso_pc_10 | 3 | 20 | 30 | 0.429 | 25 | 10 | 30 | pressure_control | 50 | ISO 80601 pressure control test scenario 201.105.10
iso_pc_11 | 3 | 50 | 20 | 0.25 | 30 | 5 | 60 | pressure_control | 50 | ISO 80601 pressure control test scenario 201.105.11
iso_pc_12 | 3 | 20 | 30 | 0.429 | 15 | 5 | 30 | pressure_control | 30 | ISO 80601 pressure control test scenario 201.105.12
iso_pc_13 | 3 | 50 | 20 | 0.25 | 25 | 10 | 90 | pressure_control | 30 | ISO 80601 pressure control test scenario 201.105.13
iso_pc_14 | 1 | 20 | 30 | 0.429 | 35 | 5 | 90 | pressure_control | 30 | ISO 80601 pressure control test scenario 201.105.14
iso_pc_15 | 1 | 100 | 30 | 0.429 | 40 | 10 | 30 | pressure_control | 30 | ISO 80601 pressure control test scenario 201.105.15
iso_pc_16 | 1 | 200 | 50 | 0.5 | 25 | 5 | 30 | pressure_control | 20 | ISO 80601 pressure control test scenario 201.105.16
iso_pc_17 | 1 | 200 | 50 | 0.5 | 25 | 10 | 60 | pressure_control | 15 | ISO 80601 pressure control test scenario 201.105.17
iso_pc_18 | 1 | 50 | 60 | 0.667 | 15 | 5 | 60 | pressure_control | 10 | ISO 80601 pressure control test scenario 201.105.18
iso_pc_19 | 0.5 | 50 | 60 | 0.667 | 25 | 10 | 60 | pressure_control | 5 | ISO 80601 pressure control test scenario 201.105.19
iso_pc_20 | 0.5 | 50 | 30 | 0.25 | 15 | 5 | 30 | pressure_control | 5 | ISO 80601 pressure control test scenario 201.105.20
iso_pc_21 | 0.5 | 200 | 60 | 0.667 | 25 | 10 | 30 | pressure_control | 5 | ISO 80601 pressure control test scenario 201.105.21

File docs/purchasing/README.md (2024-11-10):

# Purchasing documentation

Here live the source files for purchasing documentation.

All part and supplier definitions are tracked in [parts.json](parts.json).

The syntax/semantics for a part definition are as follows:

```json
  {
    "pn": "unique-identifier", // follow RespiraWorks parts numbering schema
    "notes": "Verbal description of part",
    "manufacturer": "Sprocket Corp.",
    "mpn": "sprocket-4269", // manufacturer part number
    "avg_price": 4.20, // average or nominal price in USD, manually calculated from below
    "price_unit": "cm", // assumed to be per-item if left blank
    "sources": [
      {
        "supplier": "Sprocket Depot",
        "spn": "sprocket-depot-3235", // supplier part number
        "price": 4.20, // price in USD
        "price_units": 100, // useful if price is per length or area, or in bulk
        "url": "https://www.sprocket-depot.com/product/sd-3235"
      }
    ]
  }
```

## Noteworthy

[schema]: file:///home/martin/dev/ventilator/docs/_build/html/purchasing/numbering-schema.html

* Please use unique `"pn"` codes, so they can be easily linked from other documents.
* Please use our parts numbering schema, documented in the generated docs from this section [here][schema]
* Calculate the `"avg_price"` manually based on whichever supplier(s) you think are representative
* When calculating `"avg_price"` don't forget to divide by `"price_units"` if appropriate
* All prices are in USD (for now)

## Scripts

The `parts.rst` file, with tables and link nodes will be generated as when you run [docs/docs.sh build](../docs.sh).

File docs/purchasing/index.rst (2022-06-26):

Purchasing documentation
========================

This section provides information on how to obtain parts necessary for building the ventilator. The parts catalog links inventory items to suppliers, with price estimates and URLS.

.. toctree::
   :maxdepth: 2

   purchasing-guidelines
   numbering-schema
   parts

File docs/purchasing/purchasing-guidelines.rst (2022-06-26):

Parts purchasing guidelines
---------------------------

If you are a member of the RespiraWorks team, please don't buy anything using personal funds (we need to document everything in specific ways to meet the requirements of our grant funding).

Before purchasing any parts, **ask** team members if they have any spare parts floating around. There are a lot of extras, so you may be able to get your hands on parts without ordering anything.

Particularly, take note of components that may require special tools. Perhaps someone else on the team has purchased the tools and can manufacture the parts without you having to also buy specialized tools.

When selecting parts to purchase, please note that the supplier links are only suggestions. Prices and shipping times are in flux. To the extent you can, try to find a similar product that can get to you faster. What you order doesn't have to come from the same supplier as listed.

If you do need to purchase parts, follow the process below. Note: This process is subject to change as we work out any issues. Message Curtis Kline with any questions.

1. If you need to buy something, put the details into a post in `#purchasing-sourcing <https://respiraworks.slack.com/archives/C011FD2TEQM>`_ (RespiraWorks Slack channel) and tag the `@purchasing <https://respiraworks.slack.com/admin/user_groups>`_ group.
2. One of the Purchasing team members will source the items and confirm with you before placing the order.
3. Everything will be purchased using a RespiraWorks credit card whenever possible.
4. The Purchasing team member will reply to your message in `#purchasing-sourcing <https://respiraworks.slack.com/archives/C011FD2TEQM>`_ with tracking info when available.
5. In the rare case that you do buy something urgent with your own payment methods, submit your receipts to #accounting-reimburse.

Doing your part
^^^^^^^^^^^^^^^

As part of the collaborative effort of this open source project, we would very much appreciate your contribution in proofreading our pages and ensuring that the documentation is up to date.

If, while ordering components, you notice any:

* discontinued parts
* significant price changes
* need to obtain parts from alternative supplier (i.e. in a different region/country)

In such cases please either:

* notify someone on the engineering team
* (better) make a github ticket identifying errors/deficiencies
* (best!) edit the page and make a pull request! (but please read `wiki <https://github.com/RespiraWorks/Ventilator/wiki>`_ for contributor guidelines)

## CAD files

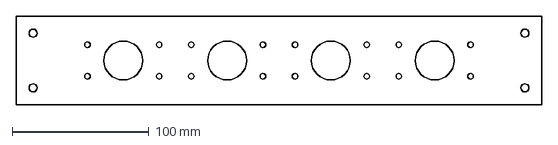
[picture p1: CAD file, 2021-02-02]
manufacturing/internals/filter_panel/filter_panel_acrylic_plate.dxf
385.0 x 65.0 mm

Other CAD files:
manufacturing/enclosure/back.ipt
manufacturing/enclosure/bottom.iam
manufacturing/enclosure/bottom.ipt
manufacturing/enclosure/cooling_fan/cooling_fan.iam
manufacturing/enclosure/enclosure.iam
manufacturing/enclosure/front.ipt
manufacturing/enclosure/internal_volume.ipt
manufacturing/enclosure/side.iam
manufacturing/enclosure/side.ipt
manufacturing/enclosure/side_left.iam
manufacturing/enclosure/side_left.ipt
manufacturing/global_params.ipt
manufacturing/internals/PSOL/PSOL.iam
manufacturing/internals/air_check_valve/blower_check_valve.iam
manufacturing/internals/back_panel/back_panel.iam
manufacturing/internals/back_panel/back_panel_acrylic.ipt
manufacturing/internals/back_panel/data_port_panel.iam
manufacturing/internals/back_panel/data_port_panel_acrylic.ipt
manufacturing/internals/back_panel/main_power_panel.iam
manufacturing/internals/back_panel/main_power_panel_acrylic.ipt
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

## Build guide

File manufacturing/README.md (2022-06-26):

# Manufacturing design

|      Full assembly rendering      |                  Internals                   |
|:---------------------------------:|:--------------------------------------------:|
|  |   |

This section of the repository describes the physical design of the ventilator and the process of manufacturing the components and fully assembled units.

## DISCLAIMERS

**This is an incomplete, as yet untested design that is not intended to be used on patients.**

**The repository contains live documents. All documentation here is on a "best effort" but no guarantee basis. Information is incomplete. Pictures, renderings, parts lists and fabrication instructions may contradict each other. Components may or may not connect and integrate as intended. Contents may also be out of date. If you decide to buy or build anything, do so at your own risk.**

**FIRE HAZARD** The below design is not fundamentally safe to be used or tested with oxygen or other volatile gases. Parts of the pneumatic design address the need for controlled pressurized oxygen supply. These aspects of the design have only been tested with pressurized air as proof of concept. Listed components are not safe to use with concentrated oxygen. Oxygen is a volatile substance and at high concentration is an extreme fire hazard. Do not do anything stupid.

**No endorsements.** Materials listed in these pages include links to various suppliers. This does not constitute any endorsement of specific products nor indication that those components are appropriate and reliable for use in medical devices. These links are simply here for our own convenience, since we all use the repository as our common collaboration space.

**Acknowledgements:** The following pages contain CAD models for various off-the-shelf components, such as valves, fittings and screws. These have been provided by various suppliers on their websites and may be intellectual property of the respective manufacturer. These models come with no guarantees and do **NOT** fall under the [Apache license](../LICENSE) which generally applies the rest of our project.

We are currently in the process of designing our v0.4 prototype, plans whereof are captured in some of our outstanding [Milestones](https://github.com/RespiraWorks/Ventilator/milestones). The `master` branch of this repository includes bleeding edge changes. Browse at your own peril. For the latest stable and tested (but also obsolete) version of the design see the [Releases](https://github.com/RespiraWorks/Ventilator/releases) page.

## Contributing

If you are a pneumatics or mechanical engineer and intend to contribute to our design, please read our [wiki](https://github.com/RespiraWorks/Ventilator/wiki), by which we mean **all of it**.

If you intend to make any physical components yourself, please become familiar with the [manufacturing methods guide](methods). And please help maintain it.

## Design principles

### Logical structure

The following pages and CAD models are structured according to the sub-assembly hierarchy that should be followed in building the ventilator. In general, each subassembly CAD model resides in its own directory and should be accompanied by a README file, any renderings, drawings or photos of the physical implementation. The readme file is there to explain the design rationale
and any non-trivial manufacturing or quality control steps necessary to produce the part.

There are directories for each custom-designed component or custom assembly involving off-the-shelf components arranged in a special way, or some mix thereof. Off-the-shelf CAD models all reside in the [third_party](third_party) directory with some categorization. If a component requires custom manufacturing, you can safely assume that the necessary files will be in its own directory.

This is a on a best effort basis, so some hardware may reside with CAD assemblies of a scope higher or lower from where they are listed in the parts tables. You should always consult both CAD and verbal documentation before attempting to build anything. It is highly advised that you have your parts and measure them to confirm expected dimensions match, as models may be imprecise.

Exported files for 3d printing or whatever other manufacturing processes are **not** in the repository. Recently exported files for manufacturing can be found on our Google Drive at
[Manufacturing/Output files v0.4](https://tinyurl.com/y4t5tz9f), maintained on a best effort basis.

### Metal frame and enclosure

The current version of the ventilator assembly is meant to demonstrate its packaging in "production" housing. Based on lessons learned from previous iterations, the ventilator uses a detachable internal assembly, to which all pneumatic components can be mounted and connected. This allows for 360 degree accessibility to components during initial assembly. When complete, this internal assembly is bolted into the enclosure, and the enclosure is screwed shut. The top-rear positioning of the removable enclosure lid provides access to components that will need routine maintenance.

We chose a sheet metal construction because:
* cheap and quick: sheet metal is cheap to fabricate. Unlike plastic parts, it doesn't require any expensive molds. This is great for prototyping stages and should also be an accessible manufacture process in many countries.
* strong and durable: stainless steel and other highly durable materials can be used. The frame and enclosure should be rigid and withstand mechanical stresses.
* staged assembly: we wanted the ability to assemble all internals outside the enclosure. The design is built around a strong bracket upon which all pneumatics and electrical equipment is installed. This makes assembly and maintenance easier. This is also useful when prototyping and making design modifications.

### Choice of hardware

* **metric** - preference has been given to metric hardware. Metric standard hardware is available worldwide, including countries that prefer imperial standard, but generally not vice versa.
* **hex drive** - screws with hex drive interface have been chosen. Phillips drive screws are prone to cam-out. Torx and other interfaces may be too exotic and supply chains may be limited in some parts of the world. Hex drive is practical and ubiquitous enough.
* **button head** - preference is given to button head screws. These are smaller and more flush with the surface than pan head or socket head screws and thus less likely to catch on clothing or other materials, and are also the least visually obtrusive.
* **predominantly M4** - where possible, we are standardizing to M4 mounting components. This is to minimize the variety of components to keep in inventory.

## Parts

> #TODO: Update BOM to match CAD

If you are a member of the team and intend to build your own prototype, please read the
[purchasing guidelines](purchasing_guidelines.md) first.

[ppg]: purchasing_guidelines.md

| Item   | Quantity | Manufacturer  | Part #                   | Price (USD) | Sources[*][ppg] | Notes                                                                              |
|--------|---------:|---------------|--------------------------|------------:|:---------------:|:-----------------------------------------------------------------------------------|
| **A1** |        1 | RespiraWorks  | [Wiring harnesses][a1rw] |       (0.0) |       Rw        | Wiring harnesses: these get integrated into the below assemblies                   |
| **A2** |        1 | RespiraWorks  | [Internals][a2rw]        |    ~1650.00 |       Rw        | Internals assembly - includes most pneumatics, electrical and computing components |
| **A3** |        1 | RespiraWorks  | [Enclosure][a3rw]        |     ~750.00 |       Rw        | Metal enclosure that contains and protects the ventilator internals                |
| **A4** |       18 | McMaster-Carr | 92095A188                |        0.10 |   [C][a4mcmc]   | M4 screws, 6mm: main bracket and closure fastening                                 |
| **A5** |        1 | RespiraWorks  | [Peripherals][a5rw]      |       72.98 |       Rw        | Indispensable components that are strictly outside of the assembly itself          |

**Total price estimate:** USD ~2472.00

[a1rw]:   wiring
[a2rw]:   internals
[a3rw]:   enclosure
[a4mcmc]: https://www.mcmaster.com/92095A188/
[a5rw]:   peripherals.md

## General assembly

Ventilator full assembly CAD model: [ventilator.iam](ventilator.iam)

> TODO: drawings

### Pre-fabrication

A number of custom components may have to be pre-fabricated by contract manufacturer:

* Main board / PCB and daughter board (in [electronics assembly](internals/electronics))
* Sheet metal components: [equipment bracket](internals/tray), [electronics support frame](internals/electronics), [display panel support frame](internals/display_panel) and [enclosure](enclosure)
* Acrylic components: [pneumatics tray](internals/tray), [display panel](internals/display_panel), [back panel](internals/back_panel) and  [filter panel](internals/filter_panel).
* Various gaskets

There are also various 3d printed components throughout the sub-assemblies. They will not be listed here explicitly. Familiarize yourself with the entire hierarchy of assemblies and print what is needed ahead of time.

Recently exported files for manufacturing can be found on our Google Drive at
[Manufacturing/Output files v0.4](https://tinyurl.com/y4t5tz9f), maintained on a best effort basis.

### Order of assembly:

* Prepare all custom wiring components `[A1]`
* Complete the internals assembly with all its sub-assemblies `[A2]`
* Insert internals assembly into enclosure `[A3]` and fasten it to the sides with 6x M4 screws `[A6]`
* Install cooling fan `[A4]` (optional)
* Attach main power harness to the PCB and install the closure panel `[A5]` using the remaining screws `[A6]`
* Attach power cables and/or human input devices listed in [peripherals page](peripherals.md)

Once the assembly is complete, you may proceed to the [software](../software) section of the repository and learn how to get its brain working.

## Additional notes

While this page is not comprehensive yet, some aspects of connecting sensor tubing and electronics may still be better covered in the (somewhat obsolete) "pizza build" [guide](../quality-assurance/testing/pizza_build).

Some aspects of the production packaged design are detailed in the first section of the (somewhat obsolete)[assembly video](https://youtu.be/2hdV5CWcLb4).

## Living prototypes

There are currently at least 3 prototypes being worked on in various locations around the world:

|                      |                                          |                                         |
|:--------------------:|:----------------------------------------:|:---------------------------------------:|
| Germantown Maryland  |         |    |
| Sunnyvale California |  |  |
| Visakhapatnam India  |        |       |

### Test equipment

To test a prototype you will need some additional components that are not strictly part of the ventilator itself, such as test lungs. There is additional information on the [testing](../quality-assurance/testing) page under the quality assurance section of the repository.

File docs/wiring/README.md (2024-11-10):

# Wiring assemblies

[WireViz]: https://github.com/formatc1702/WireViz
[schema]: file:///home/martin/dev/ventilator/docs/_build/html/purchasing/numbering-schema.html

Here live the source files for wiring assemblies. The documents are generated using
[WireViz][WireViz] and a mix of python and bash scripts.

## Creating a new assembly:

1. Add any new wiring-harness-specific parts to [docs/purchasing/parts.json](../purchasing/parts.json); don't forget to use a unique `"pn"` field so the part can be referenced from other pages. Please use our [parts numbering schema][schema] and follow examples.

3. Create a `*.yml` file as a [WireViz][WireViz] input, using the `"pn"` field to reference the same parts defined above

3. Create an `*.rst` file with the instructions, which references the `*.bom.tsv` and `*.png` files created by WireViz (same name as your `yml`, just different extensions).

4. Images for pinout diagrams or photos of assembly process should go into [docs/wiring/images](images), to be referenced in the definition files above.

5. Should you want to identify and link to parts inline in the text of the assembly instructions, you should use this syntax:
```
:ref:`[2] <ew-pre2>`
```

Where
* `[2]` can be any label you want, preferably matching the WireViz generated BOM item number
* `ew-pre2` should be replaced by whatever `"pn"` identifier

## Scripts

To render the wiring documentation, use [docs/docs.sh](../docs.sh) script as follows:

```shell
./docs.sh wire ./path/to/dir/or/file.yml
```

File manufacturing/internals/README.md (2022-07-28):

# Internal assembly

|                                   |                             |
|:---------------------------------:|:---------------------------:|
|  |  |

## Design rationale

The internals of the ventilator comprise the main active components of the machine.  To ease assembly and maintainance, they are split into three panels which are designed to be assembled or serviced outside of the enclosure, and then secured into the enclosure as a unit.  The three panels are:
 - **Pneumatics Panel**, described on this page, which hosts the main pneumatic workings of the ventilator: blower, oxygen regulator, control valves, and sensors.
 - **[Display Panel](display_panel)**, which hosts the main electrical workings of the ventilator: touchscreen, controller PCB, and device interfaces.
 - **[Filter Panel](filter_panel)**, which hosts the patient connection fittings and isolation filters.  Air enters and exits the ventilator through this panel.

### Acrylic panels

For serviceability, ventilator internals should be completely removable from the enclosure as a single assembly.
It was necessary to secure front acrylic panels (display panel and filter panel) to the main equipment bracket,
while also allowing it to lay flush with the front face of the enclosure. Heat-set inserts allow the panels to be
mounted securely without obstruction.

The sizing for the mounting holes was based on [this](https://www.pemnet.com/wp-content/uploads/sites/2/2022/06/sidata.pdf) catalog
for heat set inserts. For M4 nuts (page 5, metric table, row 6), length code 1 (5.72 mm) is small enough to fit in the
6.35mm-thick acrylic. The corresponding outer diameter for insertion i.e. acrylic mounting diameter is 5.94 mm.

> TODO: do same rationale explanation for filter housings

## Parts

**Note: If you are a member of the RespiraWorks team, review the [part purchasing guidelines][ppg]
BEFORE purchasing any parts.**

[ppg]: ../purchasing_guidelines.md

| Item    | Quantity | Manufacturer  | Part #                               | Price (USD) | Sources[*][ppg] | Notes                                                                    |
|---------|---------:|---------------|--------------------------------------|------------:|:---------------:|--------------------------------------------------------------------------|
| **A1**  |        1 | RespiraWorks  | [Equipment tray][a1rw]               |      172.13 |       Rw        | Metal+acrylic tray holding the internal assembly together                |
| **A2**  |        1 | RespiraWorks  | [Filter panel][a2rw]                 |      105.00 |       Rw        | Lower front panel assembly with air filters                              |
| **A3**  |        1 | RespiraWorks  | [Blower assembly][a3rw]              |       84.02 |       Rw        | Blower sub-assembly                                                      |
| **A4**  |        1 | RespiraWorks  | [Air check valve][a4rw]              |       21.25 |       Rw        | Air check valve sub-assembly                                             |
| **A5**  |        2 | RespiraWorks  | [Pinch valves][a5rw]                 |       22.93 |       Rw        | Proportional pinch valve sub-assemblies with tubing                      |
| **A6**  |        1 | RespiraWorks  | [Regulator assembly][a6rw]           |      201.80 |       Rw        | Oxygen pressure regulator assembly                                       |
| **A7**  |        1 | RespiraWorks  | [Proportional solenoid][a7rw]        |       97.44 |       Rw        | Proportional solenoid oxygen control valve assembly                      |
| **A8**  |        1 | RespiraWorks  | [Oxygen/overpressure manifold][a8rw] |      131.00 |       Rw        | Oxygen sensor and overpressure relief valve manifold                     |
| **A9**  |        1 | RespiraWorks  | [Venturi: air influx][a9rw]          |        2.00 |       Rw        | Venturi flow sensor, air influx variant                                  |
| **A10** |        1 | RespiraWorks  | [Venturi: oxygen influx][a10rw]      |        2.00 |       Rw        | Venturi flow sensor, oxygen influx variant                               |
| **A11** |        1 | RespiraWorks  | [Venturi: exhale][a11rw]             |        2.00 |       Rw        | Venturi flow sensor, exhale variant                                      |
| **A12** |        1 | RespiraWorks  | [Oxygen mixer][a12rw]                |        1.00 |       Rw        | Oxygen mixing chamber                                                    |
| **A13** |        1 | RespiraWorks  | [Back panel][a13rw]                  |       25.84 |       Rw        | Back panel, with oxygen and main power input                             |
| **A14** |        1 | McMaster-Carr | 53415K153                            |        1.32 |  [C][a14mcmc]   | 3/4"ID barbed elbow                                                      |
| **A15** |        1 | McMaster-Carr | 5463K648                             |        0.84 |  [C][a15mcmc]   | 3/4"ID x 3/8"ID barbed reducer                                           |
| **A16** |      ~1m | OCSParts      | 117062-5                             |   15.09 / m |  [Z][a16amzn]   | Soft 3/4"ID 1"OD tubing, for main line tubing                            |
| **A17** |       24 | McMaster-Carr | 9579K73                              |        0.61 |  [C][a17mcmc]   | Herbie clip K (22.2-24.9mm) for clamping 1"OD, main tubing               |
| **A18** |        1 | RespiraWorks  | [Display panel][a18rw]               |      220.00 |       Rw        | Display panel                                                            |
| **A19** |      ~1m | McMaster-Carr | 5894K34                              |    7.97 / m |  [C][a19mcmc]   | 1/4"ID 3/8"OD Tygon tubing, for oxygen line tubing                       |
| **A20** |        6 | McMaster-Carr | 9579K64                              |        0.50 |  [C][a20mcmc]   | Herbie clip BB (9.2-10.3mm) for clamping 3/8"OD, oxygen line tubing      |
| **A21** |      ~1m | uxcell        | a16031400ux0163                      |    1.33 / m |  [Z][a21amzn]   | 2.5 mm tubing for connecting venturis to pressure sensors                |
| **A22** |        1 | McMaster-Carr | 2974K392                             |        0.82 |  [C][a22mcmc]   | sensing tube 3/23" y-junction, for teeing off to patient pressure sensor |
| **A23** |        1 | RespiraWorks  | [Wiring harnesses][a23rw]            |        9.39 |       Rw        | Various wiring assemblies                                                |
| **A24** |        3 | GTSE          | GTSE-10025BLU-USSL                   |        0.04 |  [Z][a24amzn]   | Zip ties, for securing sensor tubing and wiring harnesses                |
| **A25** |        1 | RespiraWorks  | [Electronics panel][a25rw]           |      540.00 |       Rw        | Electronics panel                                                        |
| **A26** |        1 | RespiraWorks  | [U-bend adapter 60°][a26rw]          |        1.00 |       Rw        | Custom U-bend adapter for 3/4" tubing with 60° turn                      |
| **A27** |        1 | RespiraWorks  | [U-bend adapter 90°][a27rw]          |        1.00 |       Rw        | Custom U-bend adapter for 3/4" tubing with 90° turn                      |

**Total assembly price:** USD ~1650.00

[a1rw]:    tray
[a2rw]:    filter_panel
[a3rw]:    blower
[a4rw]:    air_check_valve
[a5rw]:    pinch_valve
[a6rw]:    regulator
[a7rw]:    PSOL
[a8rw]:    manifold
[a9rw]:   venturi
[a10rw]:   venturi
[a11rw]:   venturi
[a12rw]:   mixer
[a13rw]:   back_panel
[a14mcmc]: https://www.mcmaster.com/53415K153/
[a15mcmc]: https://www.mcmaster.com/5463K648
[a16amzn]: https://www.amazon.com/gp/product/B01LZ5ZK53
[a17mcmc]: https://www.mcmaster.com/9579K73
[a18rw]:   display_panel
[a19mcmc]: https://www.mcmaster.com/5894K34
[a20mcmc]: https://www.mcmaster.com/9579K64
[a21amzn]: https://www.amazon.com/gp/product/B01F4BJ7PI
[a22mcmc]: https://www.mcmaster.com/2974K392
[a23rw]:   ../wiring
[a24amzn]: https://www.amazon.com/GTSE-Small-Strength-Nylon-Cable/dp/B086H4TR5Y
[a25rw]:   electronics
[a26rw]:   custom_tubing_adapters
[a27rw]:   custom_tubing_adapters

## Assembly

**Note: Please see general advice in the [manufacturing methods guide](../methods).**

[Pneumatics assembly model](internals.iam)

The rough order/hierarchy of internals assembly is as follows:

1. Assemble the [equipment tray](tray) which will hold everything else
2. Install the [filter panel](filter_panel) to the equipment bracket
3. Install the [blower assembly](blower) onto the pneumatics tray
4. Attach the [air check valve](air_check_valve) to the blower assembly
5. Install 2x [Pinch valves](pinch_valve), for air influx and exhale control
    * remember to label the pinch valve wiring "inhale" and "exhale" appropriately
6. Install the [oxygen regulator assembly](regulator)
7. Install the [proportional solenoid](PSOL) valve for oxygen control

|          Step 1           |         Steps 2-7         |
|:-------------------------:|:-------------------------:|
|  |  |

8. Install the main tubing, sensors and manifolds:
    * [Manifold](manifold) - for oxygen sensor and overpressure relief valve
    * [Oxygen mixer](mixer) - for mixing air and oxygen before delivery to patient
    * [Venturi flow sensors](venturi) - in-house design of affordable flow sensors
    * Various tubing adapters `[13-15]`, `[26-27]`
    * 3/4 tubing `[16]` and clamps `[17]`
9. Install the [display panel](display_panel)
10. Install oxygen line tubing `[A19]` and clamps `[20]`

|          Step 8           | Steps 9-10 (except clamps) |
|:-------------------------:|:--------------------------:|
|  |   |

### Sensor tubing

Sensor tubing `[A21-22]` connects the venturis to pressure sensors in the electronics assembly.

The tubes you will use will vary in length. Use your own discretion.

Use the following principles to guide this process:
* The venturis have arrows embossed on the sides indicating flow direction. You can thus determine which of the two
  sensor ports is "upstream" vs. which one is "downstream".
* The differential sensors on the PCB (or daughter-card) have 2 ports each:
  * the upper port (further from board) is for upstream
  * the lower port (closer to board) is for downstream

Connect the tubing as follows
* upstream port on the `air influx venturi` to upper port on the `INHALE FLOW` sensor on the PCB
* downstream port on the `air influx venturi` to lower port on the `INHALE FLOW` sensor on the PCB
* downstream port on the `exhale venturi` to lower port on the `EXHALE FLOW` sensor on the PCB
* upstream port on the `exhale venturi` to wye splitter `[A22]`
* wye splitter `[A22]` to the upper port on the pressure sensor on the daughter-card
* wye splitter `[A22]` to the upper port on the `EXHALE FLOW` sensor on the PCB
* the lower port on the pressure sensor on the daughter-card remains open to atmosphere
* upstream port on the `oxygen influx venturi` to upper port on the `PATIENT PRESSURE` sensor on the PCB
* downstream port on the `oxygen influx venturi` to lower port on the `PATIENT PRESSURE` sensor on the PCB

>**TODO:** update drawings with updated tubing (O2 venturi on U3 / patient pressure on the daughter-card)
> This allows us to take advantage of the higher maximum pressure of the MPXV5010DP sensor on the daughter-card.

|           Air influx           |         Oxygen influx          |  Outflow and patient pressure  |
|:------------------------------:|:------------------------------:|:------------------------------:|
|  |  |  |

### Final wiring

By this point you should have completed all the mechanical and pneumatic sub-assemblies of the ventilator.

You can now connect all the wiring (except main power):
* RaspberryPi's `USB` to touchscreen's `5V+Touch` microUSB, using `[A8]`
* RaspberryPi's `microHDMI` to touchscreen's ribbon cable
* connect blower power wires to PCB
* connect blower control wires
  * to the interim board, if you have one
  * else, to the PCB
* connect proportional solenoid to PCB
* connect oxygen sensor to interim board
* connect the pinch valves to their driver pigtails as follows:
  * top - inhale
  * bottom - exhale
* Secure wiring with zip ties `[A24]`
* Secure sensor tubing with zip ties `[A24]`, but do so lightly. Don't tighten them to the point where the
  air flow is restricted in the tubes or where the wires can't move at all.

|          Top view           |          Bottom view           |
|:---------------------------:|:------------------------------:|
|  |  |

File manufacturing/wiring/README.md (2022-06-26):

# Wiring assemblies

**DEPRECATED - this page is deprecated, as it is being migrated to Sphinx-generated documentation located at [respiraworks.github.io/Ventilator](file:///home/martin/dev/ventilator/docs/_build/html/wiring/index.html)**

> TODO: Migrate contents to Sphinx

The following page describes the custom wiring components required in the electrical assembly. Manufacturing
these components will require soldering and crimping.

For a single ventilator unit, the following custom wiring assemblies are needed:
* [Blower power](#blower-power)
* [Blower signal/control](#blower-control-cable)
* [Stepper motor pigtails (x2)](#stepper-wiring)
* [Proportional solenoid](#proportional-solenoid-valve)
* [Oxygen sensor](#oxygen-sensor-cable)

It is probably a good idea to manufacture and test these before proceeding with the rest of the mechanical assembly.

Total price estimate: USD 24.00

Stand-alone items (not in other assemblies): USD 9.39

## Parts

**Note: If you are a member of the RespiraWorks team, review the [part purchasing guidelines][ppg]
BEFORE purchasing any parts.**

[ppg]: ../purchasing_guidelines.md

| Item    | Quantity | Manufacturer    | Part #                |  Price (USD) |   Sources[*][ppg]    | Notes                                                          |
|---------|---------:|-----------------|-----------------------|-------------:|:--------------------:|----------------------------------------------------------------|
| **A1**  |       20 | JST             | SXH-001T-P0.6         |         0.10 |      [K][a1key]      | XH crimp contacts, for sensor & actuator connections           |
| **A2**  |        1 | JST             | XHP-2                 |         0.10 |      [K][a2key]      | XH 2-pin housings, for solenoid                                |
| **A3**  |        1 | JST             | XHP-3                 |         0.10 |      [K][a3key]      | XH 3-pin housings, for oxygen sensor                           |
| **A4**  |        1 | JST             | XHP-6                 |         0.12 |      [K][a4key]      | XH 6-pin housings, for blower control                          |
| **A5**  |        7 | JST             | SVH-21T-P1.1          |         0.11 | [K][a5key] [R][a5rs] | VH crimp contacts, for main power, for blower power            |
| **A6**  |        2 | TE              | 1-1123722-2           |         0.18 | [K][a6key] [R][a6rs] | VH housing 2 pin, for blower power                             |
| **A10** |        8 | TE Connectivity | 102107-3              |         0.47 |     [K][a10key]      | 2.54mm male pin, for stepper interface                         |
| **A11** |        2 | TE Connectivity | 87499-7               |         0.73 |     [K][a11key]      | 2.54mm 4-pin housing, for stepper interface                    |
| **A12** |   ~2.5 m | Remington       | 16UL1007STRKIT        |     0.66 / m |     [Z][a12amzn]     | 16 AWG wire, for power cables                                  |
| **A13** |   ~1.5 m | Remington       | 22UL1015STRKIT10COLOR |     0.50 / m |     [Z][a13amzn]     | 22 AWG wire, for signal/control cables                         |
| **A14** |     ~4 m | Remington       | 26UL1007STRKIT10COLOR |     0.42 / m |     [Z][a14amzn]     | 26 AWG wire, for signal/control cables                         |
| **A15** |      (1) | WGCD            | 4330589508            |         8.99 |     [Z][a15amzn]     | XH connector kit for 2/3/4/5 pins, **alternative for A1-3**    |
| **A16** |      (1) | CQRobot         | CQRJST254-BGB         |         9.99 |     [Z][a16amzn]     | XH connector kit for 6/7/8 pins, **alternative for A1 and A4** |
| **A17** |      (1) | Chenbo          | WJ-Z01                |        11.98 |     [Z][a17amzn]     | 2.54mm connector kit, **alternative for A10 and A11**          |
| **A18** |        2 | Molex           | 22013037              |         0.20 |     [K][a18key]      | KK-series 3-pin sockets connector housing (oxygen sensor)      |
| **A19** |        4 | Molex           | 08550102              |         0.21 |     [K][a19key]      | crimp sockets for the above                                    |
| **A20** |     ~1 m | uxcell          | a11110900ux0059       |     1.32 / m |     [Z][a20amzn]     | Shrink tubing, black, 3mm diameter                             |
| **A21** |     ~2 m | uxcell          | A17032300ux0991       |     1.50 / m |     [Z][a21amzn]     | Shrink tubing, black, 4mm diameter                             |
| **A22** |   ~0.5 m | XHF             | B07WC9BGRT            |     0.95 / m |     [Z][a22amzn]     | Shrink tubing, red, assorted diameters                         |

[a1key]:   https://www.digikey.com/short/z44f8d
[a2key]:   https://www.digikey.com/short/z44f8f
[a3key]:   https://www.digikey.com/short/z44fb9
[a4key]:   https://www.digikey.com/short/z44ff8
[a5key]:   https://www.digikey.com/short/z44fjr
[a5rs]:    https://export.rsdelivers.com/product/jst/svh-41t-p11/jst-nv-vh-female-crimp-terminal-contact-16awg-svh/7620692
[a6key]:   https://www.digikey.com/short/z44fwj
[a6rs]:    https://export.rsdelivers.com/product/jst/vhr-2n/jst-vhr-female-connector-housing-396mm-pitch-2/8201172
[a10key]:  https://www.digikey.com/en/products/detail/te-connectivity-amp-connectors/102107-3/298993
[a11key]:  https://www.digikey.com/en/products/detail/te-connectivity-amp-connectors/87499-7/29911
[a12amzn]: https://www.amazon.com/gp/product/B00N51OJJ4
[a13amzn]: https://www.amazon.com/gp/product/B073SDGNKW
[a14amzn]: https://www.amazon.com/gp/product/B011JC76OA
[a15amzn]: https://www.amazon.com/gp/product/B06ZZ45G7G
[a16amzn]: https://www.amazon.com/gp/product/B079MJ1RYN
[a17amzn]: https://www.amazon.com/CHENBO-Connector-Housing-Assortment-Terminal/dp/B077X8XV2J
[a18key]:  https://www.digikey.com/en/products/detail/molex/0022013037/26433
[a19key]:  https://www.digikey.com/en/products/detail/molex/0008550102/172056
[a20amzn]: https://www.amazon.com/uxcell-Polyolefin-Insulation-Shrink-Tubing/dp/B008DFW8JA
[a21amzn]: https://www.amazon.com/uxcell-4mm-Shrink-Sleeve-Tubing/dp/B071VGQH97
[a22amzn]: https://www.amazon.com/XHF-140-PCS-Red-Wear-Resistant/dp/B07WC9BGRT

## Tools

| Item | Manufacturer | Part number        | Price($) | Sources[*][ppg] | Notes                              |
|------|--------------|--------------------|---------:|-----------------|------------------------------------|
| B1   | Preciva      | PR-3254 (PR102001) |    39.99 | [Z][b1amzn]     | Crimping tool (with connector kit) |
| B2   | NovelLife    | TS100              |    74.99 | [Z][b2amzn]     | 65W Soldering iron kit             |
| B3   | Chandler     | HG603D             |    24.92 | [Z][b3amzn]     | Heat gun, for shrink tubing        |
| B4   | Kester       | KE1107-ND          |    58.98 | [K][b4key]      | Solder                             |

[b1amzn]: https://www.amazon.com/gp/product/B07R1H3Z8X
[b2amzn]: https://www.amazon.com/NovelLife-Mini-TS100-Soldering-Digital/dp/B07D35B75T
[b3amzn]: https://www.amazon.com/Chandler-Tool-Embossing-Heat-Gun/dp/B07GC5N3QC
[b4key]:  https://www.digikey.com/en/products/detail/kester-solder/24-6040-0010/265622

**Crimper Tips:**

* Position 1 on the crimper will crimp JST XH contacts `[A1]` and Molex KK contacts `[A19]`
* Position 2 on the crimper will crimp VH contacts `[A5]`.  However, with certain gauges of wire, this crimper may bend the contact into a shrimp-like shape.  If this happens, bend the contact back straight (it should be pretty obvious as it blocks insertion)
* Position 3 on the crimper will crimp 2.54mm (aka Dupont) sockets and pins `[A10]`.
* A proper crimp should crimp the insulation in the lower half and the wire in the upper half of the crimp portion of the contact.
* The crimper kit `[B1]` comes with a lot of XH contacts, but not any VH contacts.

## Assembly

**Note: Please see general advice in the [manufacturing methods guide](../methods).**

Recently exported drawings for wiring harnesses can be found on our Google Drive at
[Manufacturing/Output files v0.4/Wiring](https://tinyurl.com/3rcj85m9).

As much as possible we should try to keep the cables one-to-one
(for example the wiring of the PCB to blower driver cables are all pin 1 to pin 1,
pin 2 to pin 2, etc. with the same connector style on both ends.

### Blower power

The power cable that comes included with the blower will be too short to reach the PCB,
so a new one must be manufactured.

* Using:
  - 16AWG 50cm in each of black and red `[A12]`
  - 4x VH crimp contacts `[A5]`
  - 2x VH 2-pin housings `[A6]`
  - Shrink tubing `[A21]`

- Instructions:
  - Crimp the VH contacts onto one end of each of the wires.
  - Slide on a few extra lengths of heat shrink tubing for cable management before you proceed.
  - Crimp the VH contacts onto the other end of the wires.
  - Push the contacts into the housings per the drawing until they click.
  - Do a gentle pull test to confirm proper seating of the contact.
  - Shrink the remaining pieces of heat shrink to make the cable more manageable.

- Total price: USD 2.87

|                     Cable Image                      |                                Cable Drawing                                |
|:----------------------------------------------------:|:---------------------------------------------------------------------------:|
| Blower Power Cable | Blower Power Cable Drawing  |

### Blower control cable

The signal cable that comes included with the blower will be too short to reach the PCB,
so a new one must be manufactured.

* Using:
  - 26AWG 50cm each of 6 different colors `[A14]`
  - 12x XH crimp contacts `[A1]`
  - 2x XH 6-pin housings `[A4]`
  - Shrink tubing `[A21]`

- Instructions:
  - Crimp the XH contacts onto one end of each of the wires.
  - Slide on a few extra lengths of heat shrink tubing for cable management before you proceed.
  - Crimp the XH contacts onto the other end of the wires.
  - Push the contacts into the housings per the drawing until they click.
  - Do a gentle pull test to confirm proper seating of the contact.
  - Shrink the remaining pieces of heat shrink to make the cable more manageable.

- Total price: USD 3.45

|                       Cable Image                        |                                  Cable Drawing                                  |
|:--------------------------------------------------------:|:-------------------------------------------------------------------------------:|
| Blower Control Cable | Blower Control Cable Drawing  |

### Stepper wiring

To power and control the pinch valves, they will need to be wired to the stepper driver boards. Two pigtails
can be produced for this purpose:

Recipe for one pigtail:
* 4x 22AWG 15cm `[A13]`
* 4x male 2.54mm crimp pins `[A10]`
* 2.54mm 4-pin housing `[A11]`

On the other end, each wire should be stripped about 5mm and solder applied to bind the threads.

It is advisable to label these pigtails to identify which stepper driver they shall be wired up to.
The same can be done for the stepper motors belonging to each pinch valve assembly.

Single pigtail price: USD 3.00

|         Pigtails         |         Stepper wires          |
|:------------------------:|:------------------------------:|
|  |  |

You will also need 2x small (about 5cm) 16AWG wires for connecting the two stepper boards together for power.

### Proportional solenoid valve

To connect the solenoid to the PCB, you will need to crimp a 2-pin XH connector to the wires.

- Using:
  - 2x XH crimp contacts `[A1]`
  - XH 2-pin housings `[A2]`
  - Shrink tubing `[A20]`

- Instructions:
  - Note that the polarity of these connections does not matter.
  - Slide a few extra lengths of heat shrink tubing onto the solenoid wires for cable management before you proceed.
  - Crimp the XH contacts onto the other end of the wires.
  - Push the contacts into the housings per the drawing until they click.
  - Do a gentle pull test to confirm proper seating of the contact.
  - Shrink the remaining pieces of heat shrink to make the cable more manageable.

- Total price: USD 0.96

|                      Cable Image                      |                                Cable Drawing                                 |
|:-----------------------------------------------------:|:----------------------------------------------------------------------------:|
| Proportional Solenoid Cable | Proportional Solenoid Cable Drawing  |

### Oxygen Sensor Cable

This cable connects the Oxygen Sensor to the Interim Board in the PCB stack.

- Using:
  - 26AWG 40cm in each of green and white `[A14]`
  - 4x KK series crimp contacts `[A19]`
  - 2x KK series 3-pin housings `[A18]`
  - Shrink tubing `[A20]`

- Instructions:
  - Strip the ends of the wires
  - Using the crimper `[B1]` in position 1, crimp 4x contacts `[A19]` onto the ends of the wires.
  - Sheathe the length of the wires in 3mm shrink tubing `[A20]` before inserting the ends into housing.
  - Insert the wires into the connector housings `[A18]`, according to the drawing, until they click.  Pin 1 is marked by a tiny '1' molded into the connector housing.
  - Do a gentle pull test to make sure that the contacts are properly crimped and seated.

- Total price: USD 2.11

|                      Cable Image                       |                                 Cable Drawing                                 |
|:------------------------------------------------------:|:-----------------------------------------------------------------------------:|
| Oxygen Sensor Cable | Oxygen Sensor Cable Drawing  |

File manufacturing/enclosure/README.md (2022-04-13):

# Enclosure

|              Front              |              Back               |
|:-------------------------------:|:-------------------------------:|
|  |   |

## Design rationale

> **TODO:** Content..

## Parts

> #TODO: Update BOM to match CAD

**Note: If you are a member of the RespiraWorks team, review the [part purchasing guidelines][ppg]
BEFORE purchasing any parts.**

[ppg]: ../purchasing_guidelines.md

| Item   | Quantity | Manufacturer  | Part #              | Price (USD) | Sources[*][ppg] | Notes                                 |
|--------|---------:|---------------|---------------------|------------:|:---------------:|:--------------------------------------|
| **A1** |        1 | RespiraWorks  | [Bottom][a1rw]      |   (?)150.00 |       Rw        | Bottom assembly                       |
| **A2** |        1 | RespiraWorks  | [Front][a2rw]       |   (?)150.00 |       Rw        | Front                                 |
| **A3** |        1 | RespiraWorks  | [Side: right][a3rw] |   (?)150.00 |       Rw        | Side panel assembly: right mirror     |
| **A4** |        1 | RespiraWorks  | [Side: left][a4rw]  |   (?)150.00 |       Rw        | Side panel assembly: left mirror      |
| **A5** |        1 | RespiraWorks  | [Back][a5rw]        |   (?)150.00 |       Rw        | Back/cover                            |
| **A6** |       20 | McMaster-Carr | 97525A415           |        0.09 |   [C][a6mcmc]   | 1/8" blind rivets (can also be 3mm)   |
| **A7** |        6 | McMaster-Carr | 96439A650           |        0.39 |   [C][a7mcmc]   | M4 self-clinching / press-fit nut     |
| **A8** |        4 | McMaster-Carr | 96439A710           |        1.21 |   [C][a8mcmc]   | M6 self-clinching / press-fit nut     |
| **A9** |        4 | McMaster-Carr | 9541K82             |        0.83 |   [C][a9mcmc]   | M6 threaded-stud bumper, used as feet |

**Total assembly price:** USD ~750.00

> #TODO: How much raw sheet metal?

[a1rw]:    #sheet-metal-fabrication
[a2rw]:    #sheet-metal-fabrication
[a3rw]:    #sheet-metal-fabrication
[a4rw]:    #sheet-metal-fabrication
[a5rw]:    #sheet-metal-fabrication
[a6mcmc]:  https://www.mcmaster.com/97525A415/
[a7mcmc]:  https://www.mcmaster.com/96439A650/
[a8mcmc]:  https://www.mcmaster.com/96439A710/
[a9mcmc]:  https://www.mcmaster.com/9541K82/

## Custom parts

All Inventor part models, assembly models and drawings are within this repo directory.

### Sheet metal fabrication

Enclosure is manufactured from 0.050" powder-coated aluminum.

Recently exported files for sheet metal components can be found on our Google Drive at
[Manufacturing/Output files v0.4/Sheet metal](https://tinyurl.com/2p89pjja).

|                               |                                 |
|-------------------------------|---------------------------------|
|  |     |
|   |   |

## Assembly

**Note: Please see general advice in the [manufacturing methods guide](../methods).**

The panels should be fastened together using stainless steel blind rivets. There
are rubber bumper feet on the bottom of the enclosure that are threaded into M6 press-fit nuts. The rubber bumpers
can be removed to allow the enclosure to be mounted to a medical cart.

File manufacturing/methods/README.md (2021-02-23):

# Manufacturing methods

Since we have to manufacture some custom components for the prototypes, it is worth trying to do so in as
reproducible a way as possible, so that we are testing (even in the prototyping phase) with components of similar
properties. Secondarily, this should help everyone get started faster and avoid having to reinvent the wheel.

**DISLAIMER:** None of the following constitutes an endorsement of the listed products. We have done no systematic
comparative study of alternate products and have no evidence to indicate that the following are the most appropriate
for any particular purpose.

**Note: If you are a member of the RespiraWorks team, review the [part purchasing guidelines][ppg]
BEFORE buying any parts.**

[ppg]: ../purchasing_guidelines.md

Below you will find advice on the following:
* [Sheet metal](#sheet-metal)
* [3d Printing](#3d-printing)
* [Gaskets](#gaskets)
* [Heat set inserts](#heat-set-inserts)
* [Acrylic panels](#acrylic-panels)
* [Flexible tubing](#flexible-tubing)
* [Tapered thread connectors](#tapered-threads)
* [Screwdrivers and hand taps](#screwdrivers)

## Sheet metal

**Hazard:** sheet metal edges may be sharp and you could hurt yourself while working with these components.
It is highly advise that you deburr, file and/or send all edges before you do any work with sheet metal parts.

## 3d Printing

We have been printing quite a few custom pneumatics and mechanical components. The following is a summary of what has
worked.

### Printers

We have been printing with SLA printers, such as:

* [Anycubic Photon](https://www.anycubic.com/collections/anycubic-photon-3d-printers/products/anycubic-photon-3d-printer)
* [Elegoo Mars](https://www.elegoo.com/collections/mars-series)

### Resin

We have been using either:
* [SirayaTech Fast](https://www.amazon.com/ABS-Like-Curing-Non-Brittle-Printing-Resin/dp/B07WFJ53LP) ABS-like resin
  (comes in various colors)
* The above mixed with ~30% [SirayaTech Tenacious](https://www.amazon.com/Tenacious-Flexible-Resistant-Siraya-Tech/dp/B07PLJ9XW9)
  to mitigate brittleness
  * If you have problems with parts cracking from impacts, try this mix.  It strong but slightly flexible, which makes
    it resistant to cracking.
  * The densities are similar so it doesn't matter too much if you mix it by mass or volume.  If you have a scale, you
    can mix it by mass right in the bottle, and this may reduce mess.
* [SirayaTech Clear V2](https://www.amazon.com/Blu-Strong-Precise-Resolution-Printing/dp/B083DLSR1W) Nearly transparent,
  but harder to print with. Good for things like filter housings that need to look good but don't require precision
  and strength.

Guides for printing and curing are provided on the [manufacturer's website](https://siraya.tech/pages/support).

### Slicing

Software included with lower-end SLA printers may not be the most up-to-date. We have found it useful to scaffold and
slice the models using [ChituBox](https://www.chitubox.com/). It is available for free and runs on most operating
systems, including Linux.

The following are configuration profiles we have used in Chitubox for some of the above-mentioned printer-resin combinations:
* [Anycubic Photon & Fast resin](AnyCubic_Photon_Siraya_fast_profile.cfg)
* [Anycubic Photon & 70:30 Fast:Tenacious blend](AnyCubic_Photon_Fast7_+_tenacious3_profile.cfg)
* [Anycubic Photon & Blu Clear 2 resin](AnyCubic_Photon_Siraya_Blu_Clear_2_profile.cfg)
* Elegoo Mars & Fast Resin: the default settings in Chitubox for Printer: "Elegoo Mars" and Resin: "Elegoo Standard Resin Grey for 0.05mm" work perfectly.
* [Elegoo Mars & 70:30 Fast:Tenacious blend](Elegoo_Mars_70fast_30tenacious_profile.cfg)
  * This is exactly the same as the Elegoo Standard Grey resin profile, except with lifting speed reduced to 60mm/min to prevent layer separation issues.

There is a page with additional advice on using Chitubox with the Anycubic Photon printer
[here](https://all3dp.com/2/chitubox-anycubic-photon-settings-profile/).
The Elegoo Mars works natively with chitubox.

### Kind request

When you print a new part, you may customize the scaffolding which provides some improvement over the defaults. If you
have used Chitubox to do this, please save a `*.chitubox` of your intermediate object before slicing, and upload this
file to share with others. This will save everyone time and, again, improve consistency across the team. You may
also provide whatever final printer-specific files, such as `*.photon`.

Please:
* reference version of CAD model that was rendered for printing
* add any new binary file types to be tracked by [git LFS](https://github.com/RespiraWorks/Ventilator/wiki#adding-new-binary-files).

### Post-printing finishing

For finer pieces that require tighter fits and smoother edges, you might find it useful to have
a set of [needle files](https://www.grainger.com/product/23N602).

## Gaskets

For cutting gaskets, you can use a
[craft knife](https://www.amazon.com/Fiskars-167110-1001-Heavy-Craft-Knife/dp/B001A42CTW).

## Heat set inserts

A number of components may have to be mounted using heat-set inserts in lieu of nuts. These may go into
either acrylic of 3d-printed parts. The following describes how to install them.

First off, you will need a soldering iron. It need not be an expensive one you would use for assembling electronics.
In fact, you should prefer a bulkier one, such one used for wood-burning crafts, such as
[this](https://www.amazon.com/Walnut-Hollow-Versa-Temp-Temperature-Woodburning/dp/B005P1TRAS).

1. Select a soldering iron tip large enough to provide uniform pressure on the center of the heat-set insert, but small
   enough to not touch the surrounding material.
2. Heat up your soldering iron to an operating temperature of around 343-399&deg;C (650-750&deg;F).
3. Place the heat-set insert into the mounting hole with the smaller diameter facing down into the hole away from you.
4. Touch the tip of the soldering iron to the top of the heat-set insert and wait for a few seconds.
5. The weight of the soldering iron should gently push the heat-set insert into the now melted plastic.
6. Press down slowly until the half the heat-set insert inserted into the plastic. At this point only the first set of
   knurls should be inside the plastic.
7. Allow the plastic to cool. Then push inserts in all the way till it is flush with the face of the plastic.
8. Remove heat and allow to cool and harden.

Works best if you push each of the inserts you are working on halfway, let them cool and come back to finish
them in turn.

| Start (step 4)             | Half-way (step 6)           |
|:--------------------------:|:---------------------------:|
| |  |

## Acrylic panels

We have a number of acrylic panels in the enclosed prototype. Clear acrylic was partly chosen because it
can be easily modified while quickly iterating our design, certainly more easily than any metal components.

Ideally, acrylic panels should be cut by laser. They can be cut precisely to specification.

>*TODO:* add section on laser cutters, settings, etc..

### Acrylic and hand-tools

You may not have access to a laser cutter. Or you may need to make a quick modification that does not warrant
creating a whole new CAD model and producing a part from scratch.

Common woodworking tools are perfectly adequate for modifying acrylic panels. Some of the following might be useful:

| Item   | Manufacturer   | Part #             | Price (USD)  | Sources[*][ppg] | Notes |
| ------ | -------------- | -------------------| ------------:|:---------------:|:------|
| **B1** | Black & Decker | BDEJS300C          | 24.49        | [A][b1amzn]     | Jigsaw, for cutting acrylic |
| **B2** | Black & Decker | BDEDMT             | 29.99        | [A][b2amzn]     | Electric hand drill, **drill press preferred if you have one**, for drilling acrylic |
| **B3** | XLCMSY         | EAN: 0742880496381 | 12.99        | [A][b3amzn]     | Cobalt metric drill bits, in particular - 4.5mm |
| **B4** | Porter Cable   | PC1014             | 59.59        | [A][b4amzn]     | Forstner bits, **preferred for drill press** |
| **B5** | KATA TOOLS     | KTL89020           | 19.99        | [A][b5amzn]     | Hole saws, **preferred for hand drill** |

[b1amzn]: https://www.amazon.com/BLACK-DECKER-Jig-Amp-BDEJS300C/dp/B00OJ72L84
[b2amzn]: https://www.amazon.com/BLACK-DECKER-BDEDMT-Matrix-Driver/dp/B0094B9BHE
[b3amzn]: https://www.amazon.com/XLCMSY-Straight-Resistant-Stainless-1-5-6-5mm/dp/B07ZQGXWGL
[b4amzn]: https://www.amazon.com/PORTER-CABLE-PC1014-Forstner-Bit-14-Piece/dp/B004TSZEB4
[b5amzn]: https://www.amazon.com/KATA-19-152mm-Mandrels-Installation-Plywood/dp/B08JCHY2DM

You might also want to use some 200 grit sandpaper to clean up the edges of the pieces you cut and drill.

## Flexible tubing

We have been using various types of rubber, silicon and Tygon tubing. Not all cut easily with the same type of tools.
Sometimes a [PVC pipe cutter](https://www.amazon.com/gp/product/B07Y997XKC) has worked well, other times - household
scissors or a sharp knife will do.

You may have to clamp tubing to barbed fittings, or you may want to remove the clips so that you can remove the tubing.
These [self-adjusting pliers](https://www.amazon.com/gp/product/B008S0FVWG) have proven themselves useful for either
task.

## Tapered threads

Use PTFE tape ([McMaster](https://www.mcmaster.com/6802K11/) or [Amazon](https://www.amazon.com/gp/product/B01L2F428C))
on all tapered thread joints, such as NPT. The tape not only ensures a tighter seal, but also makes it go in easier and
prevents it from seizing up if you do eventually need to remove the part.

Make sure you wrap it in the same direction as the threads will go in. There are videos online on how
to do this correctly.

You may need an [adjustable wrench](https://www.amazon.com/GETUPOWER-10-Inch-Adjustable-Opening-Vanadium/dp/B07RGV2VK1)
as well, though depending on the type of fitting you are attempting to thread pliers might also work.

## Screwdrivers

Most of the screws in the ventilator assembly require a metric hex-shaped driver.

If you already have some sort of socket driver, you could just get some
[metric hex bits](https://www.amazon.com/Wiha-71397-Metric-Insert-6-Piece/dp/B0084B7S70).

If you got nothing, a cheap choice would be a set of
[hex key wrenches](https://www.amazon.com/TEKTON-Wrench-Metric-30-Piece-25253/dp/B00I5TH074).

For something more comfortable and versatile, you could also go with a
[precision screw driver set](https://www.amazon.com/gp/product/B07R9VTWG5).

There may be a few components that require tapping or chasing of printed threads. The dedicated parts pages
will hopefully identify the exact type of tap you need. However, you may need a handle to operate these taps.

Something like [this set](https://www.amazon.com/gp/product/B003GKJYKI) should be able to handle the range of diameters
of the taps listed.

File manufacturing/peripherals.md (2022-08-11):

# Peripheral components

These components are not stricly part of the ventilator assembly, but they may be necessary to get the prototype to
work. The most obvious of these would be the power supply cables. Other devices might also be needed depending on
how you intend to deploy software, test and control the prototype.

## Parts

**Note: If you are a member of the RespiraWorks team, review the [part purchasing guidelines][ppg]
BEFORE purchasing any parts.**

[ppg]: purchasing_guidelines.md

| Item | Quantity | Manufacturer  | Part Number        | Price (USD) | Sources[*][ppg] | Notes |
| ---- |---------:| --------------| ------------------ | -----------:|:---------------:| ----- |
|**A1**| 1        | Mean Well     | GSM160A12-R7B      | 63.99       |   [K][a1key]    | 12v Power supply adapter, medical grade, 11.5A |
|**A2**| 1        | Cablelera     | ZWACPCAY-10        | 8.99        |   [Z][a2amzn]   | Hospital grade power cord |
|**A3**| (1)      | Anker         | 68ANREADER-B2A     | 12.99       |   [Z][a3amzn]   | microSD-USB adapter, for flashing RasPi images |
|**A4**| (1)      | Monoprice     | 3896               | 0.83        |  [Z][a4amzn]    | USB-A to miniUSB-B cable, for programming the nucleo |
|**A5**| (1)      | VicTsing      | IC192305US         | 23.99       |   [Z][a5amzn]   | Wireless keyboard and mouse, for setting up Rpi, **OPTIONAL** |

**Essentials (A1+A2):** USD 72.98

[a1key]:  https://www.digikey.com/en/products/detail/mean-well-usa-inc/GSM160A12-R7B/7703457
[a2amzn]: https://www.amazon.com/Cablelera-North-American-Hospital-ZWACPCAY-10/dp/B00GP6CB5A
[a3amzn]: https://www.amazon.com/Anker-Portable-Reader-RS-MMC-Micro/dp/B006T9B6R2
[a4amzn]: https://www.amazon.com/AmazonBasics-USB-2-0-Cable-Male/dp/B00NH13S44/
[a5amzn]: https://www.amazon.com/VicTsing-Keyboard-Adjustable-Independent-Indicator/dp/B07TT3VN4X

### Power

Once the ventilator is assembled, you may use `[A1]` and `[A2]` power it.

You may also want to use `[A4]` to connect the controller to your PC from which you will be flashing
controller firmware.

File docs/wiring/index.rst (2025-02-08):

.. _wiring:

Wiring Documentation
======================

.. toctree::
   :maxdepth: 2

   power_entry
   oxygen_sensor
   blower_TK_BA7050H12B
   pinch_valve

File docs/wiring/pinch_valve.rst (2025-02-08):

.. _Pinch Valve Harness:

Pinch Valve Harness
======================

.. csv-table:: **BOM**
   :widths: 5, 60, 5, 5, 5, 10, 10, 10
   :header-rows: 1
   :delim: 0009
   :file: ./pinch_valve.bom.tsv

Wiring diagram

You will need all the tools listed.

* Using items from above BOM as well as:
   * 5mm heat shrink tubing [:ref:`ew-shrink5`]
   * Heat gun
   * Molex Micro-Fit 3.0 Crimper [:ref:`te-microfit-crimper`]
   * Wire Strippers

* Instructions:
   #. In this procedure all we need to do is heat shrink the pinch valve's wires for cleanliness and apply a connector to the pigtail wires.
   #. Cut 3 pieces of the 5mm heat shrink tubing, each 5mm long, and place them over all 4 wires.
   #. Distribute the heat shrink pieces evenly along the wires' length and heat shrink them in place.
   #. Strip the appropriate length of insulation from each wire for Micro-Fit 3.0 crimp contacts.
   #. Crimp the Micro-Fit contacts to the end of each one.
   #. Insert each contact into the Micro-Fit connector housing, according to the wiring diagram.  Pin 1 is indicated by a raised stripe molded into the connector housing.
   #. Do a gentle pull test to confirm proper seating of the contacts.

Total price: USD 2.00

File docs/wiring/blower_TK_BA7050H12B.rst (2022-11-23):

.. _Blower Harness:

Blower Harness for TKFAN BA7050H12B
======================

.. csv-table:: **BOM**
   :widths: 5, 60, 5, 5, 5, 10, 10, 10
   :header-rows: 1
   :delim: 0009
   :file: ./blower_TK_BA7050H12B.bom.tsv

Wiring diagram

You will need all the tools listed.

* Using items from above BOM as well as:
   * 3mm heat shrink tubing [:ref:`ew-shrink3`]
   * 5mm heat shrink tubing [:ref:`ew-shrink5`]
   * Heat gun
   * Molex Micro-Fit 3.0 Crimper [:ref:`te-microfit-crimper`]
   * Wire Strippers
   * Soldering iron
   * Solder
* Instructions:
   #. Cut 3 pieces of the 5mm heat shrink, 15mm long each.
   #. Thread the 5mm heat shrink onto the the entire bundle of 4 wires on the blower.  Do not shrink the heat shrink yet.
   #. Insert the 2x pre-crimped Mega-Fit wires into the Megafit 2x2 housing.
   #. Do a gentle pull test to confirm proper seating of the contacts.
   #. Cut the cable at a length of 50mm from the connector.
   #. Strip 5mm of insulation from the end of the pre-crimped wires and from the ends of the red and black pigtails of the blower.
   #. Cut 2 pieces of 3mm heat shrink, 15mm long.
   #. Take the 2 pieces of heat shrink and slide one each onto the red and black wires of the blower.
   #. Solder the red and black wires to the Mega-Fit connector cables according to the diagram (pin 1 on the Mega-Fit connector is indicated by a stripe on the connector body).
   #. Slide the heat shrink over the soldered portion and use the heat gun to shrink them in place.
   #. Strip the insulation from the blue pigtail of the blower, using the Micro-Fit crimp contact as a guide for the legth of insulation to strip.
   #. Using the micro-fit crimper, crimp the contact onto the end of the blue wire.
   #. Insert the contact and wire into the micro-fit connector housing according to the diagram.
   #. Do a gentle pull test to confirm proper seating of the contacts.
   #. On the yellow blower wire, cut off any uninsulated portion from the end of the wire and place a 5mm long piece of 3mm heat shrink tubing on the end and heat shrink it in place.
   #. Distribute the 5mm heat shrink tubing evenly along the harness bundle and shrink them with the heat gun.

Total price: USD 4.00

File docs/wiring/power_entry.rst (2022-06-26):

.. _main_power_input:

Main power input
======================

.. csv-table:: **BOM**
   :widths: 5, 60, 5, 5, 5, 10, 10, 10
   :header-rows: 1
   :delim: 0009
   :file: ./power_entry.bom.tsv

Wiring diagram

You will need all the tools listed.

* Using items from above BOM as well as:
   * 5mm heat shrink tubing [:ref:`ew-shrink5`]
* Instructions:
   #. Insert the 4 pre-crimped cables :ref:`[2] <ew-pre2>` into the 2x2 Mega-Fit housing :ref:`[6] <ec-mega4>`.
   #. Clip the crimped ends off the remaining free end of the cables.
   #. Slide 15mm of heat shrink onto each of the 2 cables that will go to the DIN receptacle.
   #. Slide on a few extra lengths of heat shrink tubing for cable management before you proceed.
   #. Solder the cables to the DIN receptacle :ref:`[3] <ec-dinf4>` per the cable drawing.  Apply the heat shrink to the junction.
   #. Crimp the QC terminals :ref:`[4] <ec-qctf>` per the drawing.
   #. Crimp the ring terminal :ref:`[5] <ec-ring>` per the drawing.
   #. Do a gentle pull test to confirm proper seating of all the contacts.
   #. Shrink the remaining pieces of heat shrink to make the cable more manageable.

Total price: USD 8.94

.. todo:: move over and add pictures of soldering process

.. todo:: add prices

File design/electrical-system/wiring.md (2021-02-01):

# Wiring

**DISCLAIMER: These are live documents.
There are duplicate and alternative items for undecided aspects of the physical design.
RespiraWorks may or may not compensate you for any of these parts if you choose to buy them. Please connect with Edwin or Ethan first.
If you decide to buy them, do so at your own risk... oh, and thank you ;).**

**TODO:** explain purpose and contents

## Parts

**Note: If you are a member of the RespiraWorks team, review the [part purchasing guidelines][ppg]
BEFORE purchasing any parts.**

[ppg]: ../../manufacturing/purchasing_guidelines.md

| Item  | Quantity | Manufacturer  | Part #              | Price (USD)  | Sources[*][ppg]       | Notes |
| ----- |---------:| ------------- | ------------------- | ------------:|:---------------------:| ----- |
|**A1** |       12 | JST           | SXH-001T-P0.6       |         0.10 | [K][a1digi]           | XH crimps, for sensor & actuator connections |
|**A2** |        - | JST           | XHP-2               |         0.10 | [K][a2digi]           | XH 2-pin housings, for solenoid |
|**A3** |        - | JST           | XHP-3               |         0.10 | [K][a3digi]           | XH 3-pin housings, for heater |
|**A4** |        - | JST           | XHP-5               |         0.12 | [K][a4digi]           | XH 5-pin housings, for sensors |
|**A5** |        2 | JST           | XHP-6               |         0.12 | [K][a5digi]           | XH 6-pin housings, for blower control |
|**A6** |        - | WGCD          | 4330589508          |         8.99 | [Z][a6amzn]           | XH connector kit for 2/3/4/5 pins, alternative for 1+2+3+4 above |
|**A7** |        - | CQRobot       | CQRJST254-BGB       |         9.99 | [Z][a7amzn]           | XH connector kit for 6/7/8 pins, alternative for 1+5 above |
|**A8** |        6 | JST           | SVH-21T-P1.1        |         0.11 | [K][a8digi] [R][a8rs] | VH crimps, for main power, for blower power |
|**A9** |        2 | TE            | 1-1123722-2         |         0.18 | [K][a9digi] [R][a9rs] | VH housing 2 pin, for blower power |
|**A10**|        1 | JST           | VHR-3N              |         0.14 | [K][a10digi]          | VH housing 3 pin, for main power |
|**A11**|        1 | AIMHD         | AHD-DC20-F-PT       |    9.99 / 20 | [Z][a11amzn]          | Female Power Pigtail DC 5.5mm x 2.1mm Connectors, for main power |
|**A12**|        - | Remington     | 16UL1007STRKIT      |        29.70 | [Z][a12amzn]          | 16 AWG wire, for blower power cable |
|**A13**|        - | Remington     | 26UL1007STRKIT10COLOR |      31.60 | [Z][a13amzn]          | 26 AWG wire, for signal/control cables |
|**A14**|        - | Remington     | 22UL1015STRKIT10COLOR |      37.75 | [Z][a14amzn]          | 22 AWG wire, for signal/control cables |

[1digi]:   https://www.digikey.com/short/z44f8d
[2digi]:   https://www.digikey.com/short/z44f8f
[3digi]:   https://www.digikey.com/short/z44fb9
[4digi]:   https://www.digikey.com/short/z44r0b
[5digi]:   https://www.digikey.com/short/z44ff8
[a6amzn]:  https://www.amazon.com/gp/product/B06ZZ45G7G
[a7amzn]:  https://www.amazon.com/gp/product/B079MJ1RYN
[a8digi]:  https://www.digikey.com/short/z44fjr
[a8rs]:    https://export.rsdelivers.com/product/jst/svh-41t-p11/jst-nv-vh-female-crimp-terminal-contact-16awg-svh/7620692
[a9digi]:  https://www.digikey.com/short/z44fwj
[a9rs]:    https://export.rsdelivers.com/product/jst/vhr-2n/jst-vhr-female-connector-housing-396mm-pitch-2/8201172
[a10digi]: https://www.digikey.com/short/z44fwp
[a11amzn]: https://www.amazon.com/Connectors-Upgraded-Surveillance-Transformer-Connection/dp/B0768V9V5Q
[a12amzn]: https://www.amazon.com/gp/product/B00N51OJJ4
[a13amzn]: https://www.amazon.com/gp/product/B011JC76OA
[a14amzn]: https://www.amazon.com/gp/product/B073SDGNKW

### Tools

We try to make few assumptions about what tools you have. Here are recommended tools you might need.

| Item | Quantity | Manufacturer  | Part number         | Price($) | Sources         | Notes |
| ---- |---------:| ------------- | ------------------- | --------:|-----------------| ----- |
| B1   |        1 | Preciva         | PR-3254 (PR102001)             |    39.99 | [Z][b1amzn]     | Crimping tool for HX and HV connectors |

[b1amzn]:https://www.amazon.com/gp/product/B07R1H3Z8X

**Crimper Tips:**

* Position 1 on the crimper will crimp XH contacts
* Position 2 on the crimper will crimp VH contacts.  However, with certain gauges of wire, this crimper may bend the contact into a shrimp-like shape.  If this happens, bend the contact back straight (it should be pretty obvious as it blocks insertion)
* It comes with a lot of XH contacts, but not any VH contacts.

## Assembly

As much as possible we should try to keep the cables one-to-one
(for example the wiring of the PCB to blower driver cables are all pin 1 to pin 1,
pin 2 to pin 2, etc. with the same connector style on both ends.

Pizza pneumatics

### Blower wiring

For pizza builds: You will also have to crimp connectors (**A8 + A9**) to the second end of the wiring (using **B1**) that connects the
blower driver board to the [PCB](../../pcb).

The power and signal cables that come included with the blower are too short to reach the PCB, so new ones must be
manufactured using **A1, A5, A7-A9, A12-A13**. Please follow the old cables included with blower as examples.

The new cables should each be about 42cm in length.

**#TODO:** Some sort of shrink tubing should also be used

**#TODO:** illustrate this

### Proportional solenoid valve

To connect the solenoid to the PCB, you will need to crimp a 2-pin XH connector to the wires.

**#TODO:** expand on this and illustrate this

### Oxygen sensor

**#TODO:** missing info

## Pricing totals

**#TODO:** missing info

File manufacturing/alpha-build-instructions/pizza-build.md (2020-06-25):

# Pizza Build

**WARNING: This is not intended to be used on patients and lacks a number of safety features.**

This is a ventilator prototype for testing and development.
The build consists of a functional ventilator pneumatic assembly with controller and user interface. This build is adequate for integration and systems testing.

It lacks heating, humidification, battery backup and air filtering.

It is also not enclosed like the final product and is meant to be operated in an open layout on your table, like a pizza.

It can also come in various configurations, depending on your testing needs:

| Solenoid valve setup  |  Pinch valve setup   | Blower bypass setup     |
|:---------------------:|:--------------------:|:-----------------------:|
 |  |  |

**DISCLAIMER:** These are live documents.
There are duplicate and alternative items for undecided aspects of the physical design.

RespiraWorks may or may not compensate you for any of these parts if you choose to buy them. Please connect with Edwin, Martin or Ethan first.
If you decide to buy them, do so at your own risk... oh, and thank you ;).**

## Planning

Before you start, it would be wise to plan the configuration you will build and order adequate amounts of components.
Try to plan for what you'll need in a few weeks rather than what you need now.
Supply chains are quirky and shipping times can be long, so your surprise at having missed something will soon turn to frustration.
The goal of this documentation has been precisely to help you avoid unproductive waiting. **PLAN NOW!**

Read over as much of the following documentation as you can and then come back to this point.

Now, contact the team to see if we have components in stock that we can send you.
Once you know what you are getting from "headquarters", only then should you start filling up your baskets.
Also ask the team if anything should be ordered on the company account.

## Essentials

The first thing you will need is a [Brain build](pizza-brain), which contains the computing components.

We are using 3/4" ID tube as the default standard (and adapters where needed, like to the blower and the pinch valves).
This easily can have 19mm ID tubing substituted in metric manufacturing settings (3/4" = 19.05mm).
All rigid plumbing fittings should be NPT/imperial standard (3/4 NPS preferable, to keep ID consistent throughout the flowpath).

## Parts List (BOM)

**Note: If you are a member of the RespiraWorks team, review [part purchasing guidelines](../README.md) BEFORE purchasing any parts.**

### Purchasing Source Key

* **Z** = Amazon
* **C** = McMaster-Carr

### 3/4" ID Tubing Components

| Item | Quantity | Manufacturer  | Part #              | Price (USD)     |  Sources       | Notes |
| ---- |---------:| ------------- | ------------------- | ------------:|----------------| ----- |
| a1   |      5ft |      OCSParts |            117062-5 | 22.99 / 5ft  | [Z][a1amzn]    | soft 3/4"ID 1"OD tubing |
| a2   |      5ft | McMaster-Carr | 5233K71             | 14.20 / 10ft | [C][a2mcmc]    | hard 3/4"ID 1"OD tubing, **alternative to a1**, not as fun to work with, not for medical use |
| a3   |        6 | McMaster-Carr | 9579K73             | 12.24 / 20   | [C][a3mcmc]    | Herbie clip K (22.2-24.9mm) for clamping 1"OD tubing, works better for soft tubing |
| a4   |        6 | McMaster-Carr | 9579K74             | 12.33 / 20   | [C][a4mcmc]    | Herbie clip L (24.5-27.6mm) for clamping 1"OD tubing, **alternate to a3** maybe works better for hard tubing? |
| a5   |        1 | McMaster-Carr | 5463K648            | 10.20 / 10   | [C][a5mcmc]    | 3/4"ID <-> 3/8"ID adapter, to interface with pinch valve tubing |

[a1amzn]: https://www.amazon.com/gp/product/B01LZ5ZK53
[a2mcmc]: https://www.mcmaster.com/5233K71
[a3mcmc]: https://www.mcmaster.com/9579K73
[a4mcmc]: https://www.mcmaster.com/9579K74
[a5mcmc]: https://www.mcmaster.com/5463K648

### Metric Version

**#TODO: document how to build with metric components**

### Tools

Assembling the pneumatic system will likely need the following tools.
T1 might be enough and T4 might be unnecessary.
Also, scissors or a sharp knife might be ok instead of T3.

| Item | Manufacturer  | Part number        | Price (USD) | Sources         | Notes |
| ---- |--------------:| ------------------ | -------- | ---------------:|------ |
| c1   |        TEKTON |              37122 |    13.00 | [Z][c1amzn]     | 8 inch slip-joint pliers, for clamping tubes onto fittings |
| c2   |   Duda Energy |     LPpvc075-005ft |    19.99 | [Z][c2amzn]     | Adjustable wrench, at least 1" wide opening, for screwing in NTP fittings |
| c3   |        DEWILL |          (unknown) |    15.88 | [Z][c3amzn]     | Pipe and PVC cutter, for cutting tubing |
| c4   |         IRWIN |            2078216 |     8.90 | [Z][c4amzn]     | Long nose pliers, for removing herbie clips |
| c5   |          PTFE | vanguardSealantsPTFE-01 |     6.49 | [Z][c5amzn]     | It's advisable to teflon tape all NTP threaded components. Not only will they be more airtight, but also they will be easier to tighten and release. |

[c1amzn]: https://www.amazon.com/TEKTON-2-Inch-Joint-Pliers-37122/dp/B00KLY1FAY
[c2amzn]: https://www.amazon.com/GETUPOWER-10-Inch-Adjustable-Opening-Vanadium/dp/B07RGV2VK1
[c3amzn]: https://www.amazon.com/gp/product/B07Y997XKC
[c4amzn]: https://www.amazon.com/Tools-VISE-GRIP-Pliers-6-Inch-2078216/dp/B000A0OW2M
[c5amzn]: https://www.amazon.com/gp/product/B01L2F428C

## Sub-assemblies

The following are essential sub-assemblies that you'll need no matter what additional/optional "toppings" you chose to have.

* [Blower assembly](pizza-blower) - the main driver of pressure in the pneumatic circuit
* [Basic test lung](pizza-test-lung) - something to simulate a lung
* 2x [Venturi flow sensors](../../research-development/project-venturi) and corresponding tubing, to provide the controller feedback
* Some sort of valve or valves, which leads us to...

## Optional Components

**Optional additions (toppings) for your pizza build:**
These can be added or customized based on what functions you will be developing or testing.

* **Binary solenoid:** One option for inhale or exhale valve is a binary solenoid, which either opens or closes.
The sub-assembly for this component is documented [here](pizza-binary-solenoid). The PCB can only power/control one such
solenoid, so for more advanced designs you will want to (also) start using other valves.
* **Proportional pinch valve:** A proportional pinch valve can control the airflow constriction with much better precision.
Multiple such pinch valves can be used in our prototype, the part is buildable from 3d-printed plastic components and
easily obtainable generic parts. Instructions are [here](../../research-development/project-pinch-valve).
You may need anywhere between 1 and 3 such pinch valves, depending on the complexity of your system.
* **Reduced compliance test lung:** To test basic function a ventilator check lung or a breathing bag is sufficient,
but can really only work up to 10cmH2O. To be able to test higher PIP values, you need to reduce the compliance of the
lung so you don’t just inflate it like a balloon (or pop it). View more details on reduced compliance test lung [here](pizza-compliance-test-lung).
* **#TODO: check valve**
* **#TODO: oxygen supply limb**

## Assembly Instructions

Use the following diagrams as well as the pictures of the most recent builds at the top of the page to help you assemble this lego set.

Pizza pneumatics
[Pneumatics diagram source](assets/pizza-pneumatics.eps)

Note: mind which tubes go into the bottom and top ports of the sensors on the PCB.

Pizza drawing

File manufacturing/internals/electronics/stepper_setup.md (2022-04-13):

# Stepper driver configuration

When the PCB was originally designed, the ability to add a stepper driver was essentially a hedge, a backup *just in
case* we wanted to try something that required a stepper motor, so if some of this looks hacky, that's why.  Now that
the stepper-driven valve concept is moving towards the main design, we need to support it.  This is a guide to using
stepper motors with the Rev1 PCB.

## Background reading

* For background on stepper motors in general, the always-excellent Great Scott provides a good
  [intro to stepper motors](https://youtu.be/bkqoKWP4Oy4)
* For information on the powerSTEP01, the specific driver for X-NUCLEO-IHM03A1 we are using in Rev 1.0 of the PCB,
  [there is a video here](https://youtu.be/_Arx5CMr_mk). Keep in mind that while this driver is only selected  for R&D.
  We may move to something different in the final product, as powerSTEP01 is likely to be way overkill for this
  application, but it does offer a lot of convenient features.

## Integration notes

* Note that pin naming conventions and color codes vary from manufacturer to manufacturer.
    * If it does nothing and draws no current, swap one wire from the A pair with one wire from the B pair.
    * If you send a CW command and it turns CCW, then swap the polarity of either the A or B pair, but not both.
* Set the correct chip select for the powerSTEP01 (see
  [Hardware ICD](https://docs.google.com/spreadsheets/d/1JOSQKxkQxXJ6MCMDI9PwUQ6kiuGdujR4D6EJN9u2LWg/edit?usp=sharing)
  for pin assignments)
* Send SPI commands to the powerSTEP01 from the NUCLEO to setup the motor settings.
  [sample code: pcbreathe-bringup](https://github.com/inceptionev/pcbreathe-bringup)
* Send SPI commands to the powerSTEP01 to command motions.
  [sample code: pcbreathe-bringup](https://github.com/inceptionev/pcbreathe-bringup)

## In action

dual motors moving

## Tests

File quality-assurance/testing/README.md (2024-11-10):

# Testing

This section contains testing information, including testing plans, and resulting data.

## Test equipment

The following custom in-house developed test equipment is used.

## Development prototypes - AKA "pizza build"

[DIY test lung](test_lung) - a simple test lung for prototyping purposes

[**Pizza build**](pizza_build) -  a fundamentally functional ventilator that that includes sensors, drivers and pneumatics.
It is not enclosed like the final product and is meant to be operated in an open layout on your table, like a pizza.
This page may be somewhat `OBSOLETE`, so please also read the [manufacturing](../../manufacturing) section for
information about the latest pneumatic/mechanical design decisions.

## Test data

> TODO: link to test database

Full archive of legacy (v.0.2-0.3) test data has been moved to
[Google Drive](https://drive.google.com/drive/folders/1uaE0JVirbfPbpzJjl3X7DUDbAeUo5Ja3?usp=sharing)

## Durability and Life-Leader Testing



To validate that the ventilator components are suitable for extended periods of continuous operation, we are setting up automated
durability and life-leader tests. These tests will eventually cycle both individual components and assembled ventilators over time,
measuring any change in performance. The goal is that these test units will have more cycles on them than any
operational ventilators in the field, giving us confidence that the design can withstand continued operation.

Our Preliminary Life Leader Test has focused on the custom proportional pinch valve design and the blower, the two major moving parts in the ventilator. As discussed in more detail elsewhere, the pinch valve design results in cyclical stress both on the valve and on the tubing - a key question is how
well the design will hold up over time. We have had one pinch valve running continuously for a few weeks and are doing
performance testing to see how it compares to fresh valves.  The blower operates at over 40,000 RPM and so also is a potential service life concern.  This life leader testing incorportates partial wear life acceleration: the pinch valve operates at 60 cycles/minute at 0-100% actuation, whereas in actual ventilator use, the fastest rate will be 30 cycles/minute.  The blower operates at 100% throttle, which is the highest throttle expected in practice.  This means that every hour of this prelimiary life leader test is worth 2 hours of pinch valve operation and 1 hour of blower operations.

As of 2020.09.01, 1108 hours, had elapsed on the Preliminary Life Leader Test.  This represents 3.99 million cycles on the pinch valve, representing at minimum 92 days of continuous ventilator operation at the highest setting of 30 bpm, equivalent to 2160 hours of continuous use.  On the blower, this represents 46 days of continuous operation.

**[Link to 600hr Intermediate Life Leader Test](https://drive.google.com/drive/folders/1VYlnqkLQeSA_KZ99PjS6-LAI7GFn2coH?usp=sharing)**

In the future, we will do Life Leader Testing on a full ventilator unit in order to provide a life leader for all the components.

## Status of SiL (Software-in-the-Loop) Testing

Software-in-the-loop testing is a way of testing the controller software with the modelica model such that software
development is not held up by access to hardware (testing on actual hardware would be HIL (hardware-in-the-loop)). For a
distributed team that may not have access to hardware, this can be a key way to allow the team to move quickly.
Additionally, modelica models of new components can be developed based on their data sheets before they are acquired,
allowing us to explore designs both cheaper (can evaluate components without buying them) and faster (can start updating
the software before the new hardware arrives).

We have built out the infrastructure for interfacing our controller code with modelica and tested early prototypes. We
are currently evaluating how best to integrate our existing controller code. Unfortunately, modelica relies on an
earlier version of Visual Studio to compile the external controller for it to interact with, which means it does not
support all of the C++ features that we are using. How best to work around this limitation without adding so much
overhead that SIL testing becomes more work than it is worth is still to be determined.

[More on modelica simulations](../../design/modelica.md)

## Status of Continuous Integration

We have the following automatic or automated testing and continuous integration infrastructure currently set up:

*   Cycle Controller and (New in v0.2) UI Controller unit tests being run on each commit. Only commits that pass tests
    can be merged. We use [CircleCI](https://circleci.com/), a popular continuous integration service.
*   (New in v0.2) Hardware-in-the-loop unit tests that developers can trigger manually using a shared server connected
to a development build of the device or can run against their personal device.
*   (New in v0.2) The Cycle Controller debugger tool allows automating hardware-in-the-loop tests and was used to
collect data for CoVent testing scenarios presented in 02-1 Performance Evaluation Report.
*   (New in v0.2) Continuous building of UI Controller Docker images, which also uses CircleCI.

Our near term plans also include the following:

*   Reporting of code coverage of unit tests
*   Optimizing GUI deployment with a loose coupling strategy to minimize update and development overhead:
*   Switching to Debian package management system
*   Unit tests for communications between the GUI and controller
*   Automate data analysis from unit tests to provide insight from test data

### Hardware-in-the-loop testing

There is a strategy defined for [embedded software testing](../../software/design/embedded_software_testing.md).

The goal of these tests is to test some subsets of our system with hardware on a regular basis and in a systematic way,
to increase the likelihood of catching at least some problems early.  These tests consider some cross-section of the
hardware-software stack. To avoid the "fox watching the hen-house" situation, we have aimed at using an alternative
hardware-software stack to confirm the performance of our system.

We are in the process of procuring all necessary components for this testing infrastructure, as well as building the
automation software, however some of it is already available for developers.

In particular:

*   We have set up a server connected to a build of the ventilator, which developers can access over ssh
*   We have written several tests that can be run against the device to confirm the functionality of the hardware
    abstraction layer of our software.
*   Multiple independent sensors have been procured to help confirm our code for pressure and flow sensing.
*   Modified pinch valves have been designed with additional sensors to confirm proper calibration and homing routines.
*   A Labjack data acquisition system has been obtained that will allow us to acquire validation data in an automated
    fashion.
*   The test units are powered via USB-controlled relays, allowing developers to remotely power cycle the test units.
*   A Jenkins CI server has been set up that will allow us to run all of these tests on a regular basis, same as
    software unit tests done in CircleCI.

This testing lab will remain functional for the duration of further ventilator design through final product deployment
and beyond, while any software development is taking place.



Some of the developed test infrastructure will likely inform the development of validation and testing suites for the
manufacturers of the final product.

More information about this infrastructure is available under
[software/controller/integration_tests](../../software/controller/integration_tests).

### System tests using the scriptable debug interface

Additionally, we have built a debug interface into the device, and a Python-based command-line tool that can communicate
with the device over that interface. The tool can be attached to the device even when the GUI is running.

Normally the debug tool is used simply for debugging (e.g. retrieving or overwriting values of certain system state
variables or parameters, or collecting data traces), however it is scriptable and is also used for automating testing
scenarios. As of writing, we have used the tool for automating the collection of test data for CoVent testing scenarios.
We plan to expand its use to more automated tests and apply it as part of the shared hardware-in-the-loop testing
infrastructure described above.

More information about the debug interface is available [here](../../software/tools).

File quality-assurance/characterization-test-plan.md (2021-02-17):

# Characterization Test Plan

This document will track desired characterization tests and link to the corresponding data when the test is performed.
Eventually the info from this document will likely be formalized into a record of tests that have been performed as part
of the development and validation of the ventilator - integration tests with the real software are expected to be
defined elsewhere, though they could be folded into this.

**Caution:** this document has not been formally reviewed and is a work in progress. Be responsible to understand the
provenance of documentation.

**NOTE:** these tests are supposed to be iteratively developed. As we progress, the tests will become more granular.

## System Characterization

* **Fan Tests**

**#TODO** Add content

[View fan tests](../manufacturing/internals/blower/characterization-tests)

* **PIP/PEEP/Timing Tests**

    1. What is the maximum pressure that can be achieved with the current blower with a representative amount of tubing, a fully open air inhale valve, and a fully closed exhale valve?

    2. From PEEPs of 0 to 20 cm H20 (in reasonable increments), how quickly can the current design achieve PIPs from 10 cm H20 up to 60 cm H20 (or the max value, testing reasonable increments)?

    3. From PIPs from 20 cm H20 up to 60 cm H20 (or however high can be achieved, in reasonable increments), how quickly can the system vent down to PEEPs of 0 to 20 cm H20 (testing reasonable increments)?

    4. For PIPs from 20 cm H20 up to 60 cm H20 (in reasonable increments), what is the maximum flow rate into the patient that can be achieved? How does this change as a function of how much the exhaust valve is open?

    5. For 1-4 with a flow source that is better than the blower, what can be achieved (what becomes the next lim fac)?

* **System Sensitivity Tests**

    1. What is the difference in pressure right after the inhale venturi (before the humidifier) and at the patient pressure sensor before the exhale venturi?

## Valve Tests

* **Pinch Valve Characterization**

    1. How quickly can the pinch valve be fully opened? How does this change as a function of pressure (up to at least 60 cm H20)?

    2. How quickly can the pinch valve be fully closed? How does this change as a function of pressure (up to at least 60 cm H20)

    3. What is the leak rate past a fully closed pinch valve as a function of pressure (up to at least 60 cm H20)?

* **Proportional Solenoid Characterization**

    1. How quickly can the solenoid be fully opened? How does this change as a function of pressure (up to at least 60 cm H20)?

    2. How quickly can the solenoid be fully closed? How does this change as a function of pressure (up to at least 60 cm H20)

    3. What is the leak rate past a fully closed solenoid valve as a function of pressure (up to at least 60 cm H20)?

## Sensor Tests

* **DP sensor/Venturi characterization**

    1. For flow rates from 1 to 80 lpm, how accurate is the flow measurement and how does this accuracy change over time (if sitting at a specific FiO2)?

    2. How do the measurements for letter i above change as a function of temperature and humidity?

    3. How do the measurements for letter i above change as a function of the flow rate that is being started at (e.g. if you go from 1->80 or 40->80 does the accuracy change? What about 80->1 and 80->40)?

    4. When there is a change in flow rate, how long does it take for the sensor to settle?

    [View Venturi tests](../manufacturing/internals/venturi/characterization-tests/06072020/README.md)

* **Pressure sensor characterization**

    1. For pressures from 1 to 60 cm H20, how accurate is the pressure reading and how does this accuracy change over time (if sitting at a specific FiO2)?

    2. How do the measurements for letter i above change as a function of temperature and humidity?

    3. How do the measurements for letter i above change as a function of flow rate past the sensor?

    4. How do the measurements for letter i above change as a function of the pressure that is being started at (e.g. if you go from 5->60 or 30->60 does the accuracy change? What about 60->5 and 60->30)?

    5. When there is a change in pressure, how long does it take for the sensor to settle?

* **O2 sensor characterization**

    1. For FiO2s from 21% to 100%, how accurate is the o2 sensor reading and how does this accuracy change over time (if sitting at a specific FiO2)?

    2. How do the measurements for #1 change as a function of temperature and humidity?

    3. How do the measurements from #1 change as a function of flow rate?

    4. When there is a change in FiO2, how long does it take for the sensor to settle?

## Things that need to be added

* #todo Add electronics/Software/Controller tests?

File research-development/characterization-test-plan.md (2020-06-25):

# Characterization Test Plan

This document will track desired characterization tests and link to the corresponding data when the test is performed. Eventually the info from this document will likely be formalized into a record of tests that have been performed as part of the development and validation of the ventilator - integration tests with the real software are expected to be defined elsewhere, though they could be folded into this.

**Caution:** this document has not been formally reviewed and is a work in progress. Be responsible to understand the provenance of documentation.

**NOTE:** these tests are supposed to be iteratively developed. As we progress, the tests will become more granular.

## System Characterization

* **Fan Tests**

**#TODO** Add content

[View fan tests](project-fan/characterization-tests)

* **PIP/PEEP/Timing Tests**

    1. What is the maximum pressure that can be achieved with the current blower with a representative amount of tubing, a fully open air inhale valve, and a fully closed exhale valve?

    2. From PEEPs of 0 to 20 cm H20 (in reasonable increments), how quickly can the current design achieve PIPs from 10 cm H20 up to 60 cm H20 (or the max value, testing reasonable increments)?

    3. From PIPs from 20 cm H20 up to 60 cm H20 (or however high can be achieved, in reasonable increments), how quickly can the system vent down to PEEPs of 0 to 20 cm H20 (testing reasonable increments)?

    4. For PIPs from 20 cm H20 up to 60 cm H20 (in reasonable increments), what is the maximum flow rate into the patient that can be achieved? How does this change as a function of how much the exhaust valve is open?

    5. For 1-4 with a flow source that is better than the blower, what can be achieved (what becomes the next lim fac)?

* **System Sensitivity Tests**

    1. What is the difference in pressure right after the inhale venturi (before the humidifier) and at the patient pressure sensor before the exhale venturi?

## Valve Tests

* **Pinch Valve Characterization**

    1. How quickly can the pinch valve be fully opened? How does this change as a function of pressure (up to at least 60 cm H20)?

    2. How quickly can the pinch valve be fully closed? How does this change as a function of pressure (up to at least 60 cm H20)

    3. What is the leak rate past a fully closed pinch valve as a functin of pressure (up to at least 60 cm H20)?

* **Proportional Solenoid Characterization**

    1. How quickly can the solenoid be fully opened? How does this change as a function of pressure (up to at least 60 cm H20)?

    2. How quickly can the solenoid be fully closed? How does this change as a function of pressure (up to at least 60 cm H20)

    3. What is the leak rate past a fully closed soleonid valve as a function of pressure (up to at least 60 cm H20)?

## Sensor Tests

* **DP sensor/Venturi characterization**

    1. For flow rates from 1 to 80 lpm, how accurate is the flow measurement and how does this accuracy change over time (if sitting at a specific FiO2)?

    2. How do the measurements for letter i above change as a function of temperature and humidity?

    3. How do the measurements for letter i above change as a function of the flow rate that is being started at (e.g. if you go from 1->80 or 40->80 does the accuracy change? What about 80->1 and 80->40)?

    4. When there is a change in flow rate, how long does it take for the sensor to settle?

    [View Venturi tests](project-venturi/characterization-tests/06072020/README.md)

* **Pressure sensor characterization**

    1. For pressures from 1 to 60 cm H20, how accurate is the pressure reading and how does this accuracy change over time (if sitting at a specific FiO2)?

    2. How do the measurements for letter i above change as a function of temperature and humidity?

    3. How do the measurements for letter i above change as a function of flow rate past the sensor?

    4. How do the measurements for letter i above change as a function of the pressure that is being started at (e.g. if you go from 5->60 or 30->60 does the accuracy change? What about 60->5 and 60->30)?

    5. When there is a change in pressure, how long does it take for the sensor to settle?

* **O2 sensor characterization**

    1. For FiO2s from 21% to 100%, how accurate is the o2 sensor reading and how does this accuracy change over time (if sitting at a specific FiO2)?

    2. How do the measurements for #1 change as a function of temperature and humdity?

    3. How do the measurements from #1 change as a function of flow rate?

    4. When there is a change in FiO2, how long does it take for the sensor to settle?

## Things that need to be added

* #todo Add electronics/Software/Controller tests?

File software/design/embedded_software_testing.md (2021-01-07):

# Notions on software testing
When working on embedded software, there are some things that can be tested without running on the actual target machine, and some things that can not.

Anything that involves the electrical signals obviously falls into the second category. But some functional tests also need to be performed on the actual target in order to capture issues that are specific to the hardware.

We usually distinguish three types of tests for embedded software:
* Unit tests, which I think everybody is familiar with, that can usually be run outside the actual target.
* Integration tests, which are similar to units tests but involve the electrical signals and should therefore be run on the target.
* Functional tests, which are the most complete tests and can be run either on the actual target or not, depending on their scope, and on the stage of development.

Add to those the system tests, that run not only on the chip, but with the actual equipment : real sensors, real actuators, and eventually real pneumatics, and require access to physical parameters rather than electrical signals.

## Unit tests
A unit test is a check that a specific software module does what it is supposed to, in a use case that is as narrow as possible.
It should use the actual module's code, but can replace everything else with test-specific code.

Sometimes, unit tests will involve more than one module, and this is absolutely OK.

Unless there is a very good reason to run it on the actual target, it can be performed on a different environment.

## Integration tests
Integration tests check that the software low-level layers integrate properly with the hardware. For that reason they can not be run without the hardware.

These are basically unit tests, but with hardware in the loop: They need to use the actual low-level layers, but the high level layers can be test-specific.

## Functional tests
Functional tests, which check that the software actually does what it is supposed to do, and these usually need to use the actual software in its entirety, preferably in release mode, as they are the most complete tests we run on the software.
For that reason, they are preferably run on the target chip, but this rule is not set in stone.

## System tests
System tests are very similar to functional tests, but usually differ in terms of expected results: a system test no longer checks the controller's inner variables or the electrical signals, but the physical phenomenon that comes with it.
This means they can lose their deterministic nature, and results need to be interpreted with care.
They can be run on a partial system (for example replace the RPi with a laptop), but any piece of software being tested should be integrated in the full software (to capture CPU-sensitive phenomenons for example).

# Testing on the platform

Testing on the platform is usually harder than testing on a development environment, mostly because accessing the required data (electrical signal, software variable or physical parameter) is harder.

## Access to electrical signals
In order to test the embedded software on its target, we need a way to control the input signals and check the output signals of the system we are integrating.
For example, testing the controller on its hardware may require:
* reading/writing on the serial I/O line
* checking solenoid control signal
* observing blower PWM
* setting pressure sensor signal

This means you need some test equipments that allow you to read and write those signals: oscilloscopes, PWM acquisition card, voltage source, you name it.
To allow automation, those test equipments are integrated with a test PC that controls them and checks their results.

In case reading or writing a signal is too hard to do, it is OK to replace the software integration test with a system integration test where we control the physical parameter rather than the electrical one, but these are usually harder to interpret and therefore harder to automate.

For functional tests, this can be performed without using the actual hardware signals: if our integration + unit tests show that the fan power reported on the serial I/O is a reliable representation of the actual PWM signal, it is OK to use the fan power for a functional test instead of the PWM signal.
Similarly, we can use an engineering interface to replace the sensors' reading on the low-level layer output and not worry about the actual input pin.

## Access to physical parameters

The same test equipment can be used for system tests, along with additional equipment that read the physical parameter we want to check: redundant pressure sensor, speed meter for the blower, redundant flow meter, ... Those are rarely as well integrated with the test PC since the system tests that use them are not run as often and usually performed manually.

For example a system test that involves the pressure sensor would normally require placing the sensor in a pressure-controlled chamber (this is probably doable if we have the full pneumatics and a test lung, but really hard otherwise).
If that test is not primarily destined to test the pressure sensor, using an engineering interface to replace the sensors' readings with a simulated one is OK.

## Access to inner variables
If the integration tests need access to a high level module's inner variable, make it happen. Remember it is OK to hack the high level functions for an integration test.

If a functional test wants access to a module's inner variables:
* check if these variables can this be set or observed with an accessible input or output (even if it is not a 1 to 1 link)
* otherwise, these variables need to be made available on an engineering interface.

## Engineering interface
An engineering interface is a way for test engineers to access data that is otherwise not available outside the system.

I don't think we can actually get away without one of these for functional tests (but please prove me wrong! As this is usually quite a hassle to build and test).

Since the functional tests are preferably run on the release version of the software, keep in mind the engineering interface will be included in the final product, even though it is not needed by the users. It may be hard to access to a user, but it is still there.

That interface can be a specific interface (a second UART channel?) accessible only with specific instruments (instrumented PCB for testing, ...), or an extended version of the existing interface that is dormant unless some test conditions are met (I would go that route for our needs).
This interface must :
* Have unit tests of its own to make sure it gives a reliable copy of the desired data and properly writes data at the correct place
* Prevent accidental write on the write data (secure write privilege by a discrete signal, a specific sequence to enable writing, ...)

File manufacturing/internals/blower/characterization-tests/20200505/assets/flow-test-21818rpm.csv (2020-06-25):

t | p1_adc | patient | p2_adc | p2 | p3_adc | p3 | Q1
0.05 | 457.0 | 1.186104218362283 | 580.0 | 1.7855361596009975 | 629.0 | 2.0150753768844223 | 66.27393128634002
0.1 | 448.0 | 1.1414392059553349 | 632.0 | 2.0448877805486285 | 663.0 | 2.185929648241206 | 70.92398808883199
0.15 | 480.0 | 1.3002481389578164 | 557.0 | 1.6708229426433916 | 641.0 | 2.0753768844221105 | 64.109682099571
0.2 | 461.0 | 1.205955334987593 | 638.0 | 2.0748129675810474 | 600.0 | 1.8693467336683418 | 71.44105924624942
0.25 | 482.0 | 1.3101736972704714 | 629.0 | 2.029925187032419 | 616.0 | 1.949748743718593 | 70.6640336842167
0.3 | 440.0 | 1.1017369727047146 | 601.0 | 1.8902743142144638 | 627.0 | 2.0050251256281406 | 68.1900210987737
0.35 | 435.0 | 1.0769230769230769 | 593.0 | 1.8503740648379052 | 620.0 | 1.9698492462311559 | 67.46649907706849
0.4 | 468.0 | 1.2406947890818858 | 625.0 | 2.0099750623441395 | 632.0 | 2.030150753768844 | 70.31593287908903
0.45 | 451.0 | 1.1563275434243176 | 622.0 | 1.9950124688279303 | 640.0 | 2.07035175879397 | 70.05372214776233
0.5 | 461.0 | 1.205955334987593 | 617.0 | 1.9700748129675811 | 633.0 | 2.0351758793969847 | 69.61450952869981
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

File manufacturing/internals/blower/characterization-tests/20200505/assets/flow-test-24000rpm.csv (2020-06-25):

t | p1_adc | patient | p2_adc | p2 | p3_adc | p3 | Q1
0.019 | 518.0 | 1.488833746898263 | 757.0 | 2.6683291770573567 | 746.0 | 2.6030150753768844 | 81.0173643874324
0.038 | 534.0 | 1.5682382133995036 | 787.0 | 2.8179551122194515 | 801.0 | 2.879396984924623 | 83.25789831176792
0.057 | 530.0 | 1.5483870967741935 | 708.0 | 2.423940149625935 | 717.0 | 2.457286432160804 | 77.21814323012694
0.076 | 3.725320496528184e-09 | -1.0818858560609166 | 737.0 | 2.56857855361596 | 744.0 | 2.592964824120603 | 79.48859750271231
0.094 | 526.0 | 1.5285359801488834 | 713.0 | 2.4488778054862843 | 704.0 | 2.391959798994975 | 77.61433948532223
0.113 | 505.0 | 1.4243176178660049 | 682.0 | 2.29426433915212 | 676.0 | 2.251256281407035 | 75.12424764860722
0.132 | 474.0 | 1.2704714640198511 | 705.0 | 2.4089775561097255 | 732.0 | 2.5326633165829144 | 76.97944669850344
0.151 | 505.0 | 1.4243176178660049 | 751.0 | 2.638403990024938 | 761.0 | 2.678391959798995 | 80.56178046992667
0.17 | 539.0 | 1.5930521091811414 | 752.0 | 2.6433915211970076 | 758.0 | 2.663316582914573 | 80.63788986854473
0.189 | 522.0 | 1.5086848635235732 | 674.0 | 2.254364089775561 | 700.0 | 2.371859296482412 | 74.46812811555122
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

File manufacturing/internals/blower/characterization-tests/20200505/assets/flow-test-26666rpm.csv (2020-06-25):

t | p1_adc | patient | p2_adc | p2 | p3_adc | p3 | Q1
0.05 | 585.0 | 1.8213399503722085 | 838.0 | 3.0723192019950125 | 847.0 | 3.1105527638190953 | 86.93438295406521
0.15 | 618.0 | 1.9851116625310175 | 840.0 | 3.082294264339152 | 857.0 | 3.1608040201005023 | 87.0753958333687
0.2 | 559.0 | 1.6923076923076923 | 828.0 | 3.0224438902743143 | 850.0 | 3.1256281407035176 | 86.22585946185266
0.25 | 543.0 | 1.6129032258064515 | 835.0 | 3.057356608478803 | 840.0 | 3.0753768844221105 | 86.72243371644613
0.3 | 545.0 | 1.6228287841191067 | 744.0 | 2.603491271820449 | 736.0 | 2.5527638190954773 | 80.02698796478866
0.35 | 562.0 | 1.7071960297766748 | 847.0 | 3.117206982543641 | 848.0 | 3.1155778894472363 | 87.5671526847029
0.45 | 580.0 | 1.7965260545905708 | 826.0 | 3.0124688279301743 | 845.0 | 3.100502512562814 | 86.08345497249391
0.5 | 571.0 | 1.751861042183623 | 836.0 | 3.0623441396508726 | 845.0 | 3.100502512562814 | 86.79314097133647
0.55 | 574.0 | 1.7667493796526055 | 847.0 | 3.117206982543641 | 856.0 | 3.1557788944723617 | 87.5671526847029
0.6 | 559.0 | 1.6923076923076923 | 893.0 | 3.346633416458853 | 896.0 | 3.35678391959799 | 90.73241696209243
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

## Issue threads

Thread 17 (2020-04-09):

RespiraWorks/Ventilator #17: Change PID #defines to variables

neelfirst, 2020-04-09:
Copied thread from inceptionev/FixMoreLungs:

@rwilbur We will need to change the PID #defines to variables so they can be changed via the communications to the raspberry pi

@lee-matthews Indeed. Was planning on making possible to set those too. Maybe create some kind of "engineering/debug" mode on the interface module so that we can play with these values directly that's protected from a typical user.

@rwilbur That makes sense. I am pretty sure that all these will need to be set in the UI but open to a user since nurses and doctors will need to be changing all of these based on the patient and their progress.

#define INSPIRE_TIME 1600
#define INSPIRE_RATE 1
#define PIP 142
#define INSPIRE_DWELL 800
#define INSPIRE_DWELL_PRESSURE 140
#define EXPIRE_TIME 1000
#define EXPIRE_RATE 1
#define PEEP 130
#define EXPIRE_DWELL 600

Perhaps with these we won't have these values being set directly but have it be a certain unit on the display and it gets converted to whatever these units are in the command.

@lee-matthews I was thinking of an engineering mode for the parameters for the PID for example, I don't think the medical personnel should have access to these. Same for any potential calibration parameters.

jlebar, 2020-04-15:
I've looked more closely at this.  There's a lot more to making this module work than just replacing the `#define`'ed variables with `parameter_getFoo()`.

 - Change the module to be time-based, rather than based on the number of times we call it from the main loop (which has no bearing on time).
 - Add separate inhale/exhale-dwell parameters (right now parameters and comms just have a single "dwell" param).
 - Some sort of testing.  I noticed upon code inspection that `cyclecounter` is not a static variable, so doesn't actually count anything between calls.

I also think that we should get rid of most or all of our `float` variables, eventually up through the comms layer.  There's no need to be doing floating-point math, which is expensive, error-prone, and I think unnecessary here.  AIUI our current microcontroller doesn't even support FP; maybe the only reason this compiles is that we're targeting a different chip in our `platformio.ini`?

lee-matthews, 2020-04-16:
Indeed, this needs a lot of work.
As a start I was thinking of changing the name from pid.cpp to something like controller.cpp
Then the controller module would act as an abstraction layer to the two medical ventilation mode modules, PRVC and  ACV. Each one of these would have its own FSM to control the breathing cycle. What do you think?

lee-matthews, 2020-04-16:
I've started layout out my thoughts in this branch : lee-matthews/issue103_controllerModule

Please let me know what you think.

jlebar, 2020-04-16:
> As a start I was thinking of changing the name from pid.cpp to something like controller.cpp
Then the controller module would act as an abstraction layer to the two medical ventilation mode modules, PRVC and ACV. Each one of these would have its own FSM to control the breathing cycle. What do you think?

That sounds smart to me!  My only comment ("two hard problems in computer science") is that maybe we shouldn't use the name "controller", because we're already using that word to refer to the microcontroller chip and code.  blower_controller?  Or just "blower"?  I'm really not sure what blower.cpp is supposed to do.

> I've started layout out my thoughts in this branch : lee-matthews/issue103_controllerModule

What is the base rev for the branch?  I went here and compared it to master, but I think that's (a lot) more changes than are relevant.

https://github.com/RespiraWorks/VentilatorSoftware/compare/lee-matthews/issue103_controllerModule

lee-matthews, 2020-04-16:
Yeah, that's more than likely the case as I screwed up and merged master
into issue 77 instead of the other way around. So I started the branch
issue103 based on branch issue77 so it's understandable there are more
changes in there than necessary compared to master. I'm still getting used
to github.

Yeah, I hear you on the name, I'll think of something else.

Miceuz, 2020-04-25:
One short note - PID loop has to run in a strictly periodic fashion for it to work properly. Now it's called as fast as possible. That will break as soon as we add new code to the main loop - it will de-tune PID loop, particularly Ki and Kd variables.

For PID to run properly it has to be triggered from timer interrupt.

Also in pid.cpp we have two things intermingled - PID loop driving the blower and state machine driving the inspiration/expiration. I think we should split that in two separate files. PID has to run from timer interrupt and inspire/expire fsm can be run from main loop.

jlebar, 2020-04-25:
Ugh, thanks, Albertas.

> That will break as soon as we add new code to the main loop - it will de-tune PID loop, particularly Ki and Kd variables.

And moreover it'll break because the time to run one iteration of our main loop is not fixed, right?

Miceuz, 2020-04-25:
I don't speak phase margins, but as you go from continuous domain to discrete you are fine as long as your time quantification is constant. 

Integral and differential constants are time-dependent they are constant as long as time is constant. If we introduce time jitter, they will have bigger or lesser influence cycle-to-cycle.

jlebar, 2020-04-25:
> For PID to run properly it has to be triggered from timer interrupt.

Turns out our PID library handles this.  To be perfect we might need to call it from the timer interrupt, but it's calling `millis()`, checking the time and so on.  So I don't think we need to add interrupts right now.

jlebar, 2020-04-25:
The source code for the PID library is actually pretty nice.  You can find it at `.pio/libdeps/uno/PID_ID2`.

Miceuz, 2020-04-26:
DOH! Right, I forgot this library takes care of that. Note though that currently we are on default 100ms, we never call SetSampleTime. My feeling is that this is too slow. The exact optimal PID execution time should be determined by phase margin wizard (who we still don't have?), but intuitively it should be slow enough to react to meaningful sensor readings after filtering, slow enough to provide meaningful command to actuator and fast enough to provide rise time we need. Some sources specify it at `< 0.1 * (Tblower - Tsensor)` where `Tblower` is the blower time constant and `Tsensor` is sensor filter time. Provided we can sample and filter sensor really fast compared to blower response `Tblower >> Tsensor` the good first guess is `0.1*Tblower'. Tblower can be measured by measuring step response of the blower, it's 63% of rise time when full speed command is applied. I believe our blower responds much faster than in 1 second.

Speaking of sensor sampling - to get meaningful data those also have to run on strictly stable clock so that quantization happens on equal intervals.

asmodai27, 2020-04-26:
Hi all
I have the feeling we are discussing several different topics here, which will all need adressing, but maybe not simultaneously:

1. the main "pid controller" (currently pid.cpp, tentatively renamed "respirationCtrl" in lee-matthews/issue103_controllerModule branch to avoid confusion), which sets the "target pressure", (and should manage the exhaust valve if I am not mistaken). This needs a lot of work (currently, nothing works in there), and is quite urgent as far as I understand our Alpha objectives.

2. the actual PID control loop, which activates the blower to reach "target pressure" and for which the code looks good to me (I do have access to aviation controls code to check it against, nothing sticks out), and its parameters need some tuning (sample time is one of the many parameters that need tuning), which will only happen when someone actually runs enough simulations to find proper parameters, but does not look as urgent to me.

3. the sensors, which will also need addressing, sooner rather than later to get decent readings, and for which at some point we will need to design and tune filters (including some prediction filters to have a reliable pressure assist mode), but maybe that is secondary for Alpha so long as we have reliable instantaneous readings?

jlebar, 2020-04-26:
> Speaking of sensor sampling - to get meaningful data those also have to run on strictly stable clock so that quantization happens on equal intervals.

Can you elaborate?  What's the failure mode if we don't read (say) the pressure sensor at regular intervals?

> currently we are on default 100ms, we never call SetSampleTime. My feeling is that this is too slow.

I share that feeling.

One thing I'd like me or someone to do is to move the external PID library into our code so we can modify it, see https://github.com/RespiraWorks/VentilatorSoftware/issues/174, which I just filed.  asmodai27@, it's nice to meet you -- this bug might be up your alley.

> I have the feeling we are discussing several different topics here, which will all need adressing, but maybe not simultaneously:

> the main "pid controller" (currently pid.cpp), which sets the "target pressure", (and should manage the exhaust valve if I am not mistaken). This needs a lot of work (currently, nothing works in there), and is quite urgent as far as I understand our Alpha objectives.

Correct, this is basically my outstanding https://github.com/RespiraWorks/VentilatorSoftware/pull/172.

> the sensors, which will also need addressing, sooner rather than later to get decent readings, and for which at some point we will need to design and tune filters (including some prediction filters [...]

Also correct.

closed 2020-04-26 by jlebar

Miceuz, 2020-04-27:
> > Speaking of sensor sampling - to get meaningful data those also have to run on strictly stable clock so that quantization happens on equal intervals.
> 
> Can you elaborate? What's the failure mode if we don't read (say) the pressure sensor at regular intervals?
> 

It's the same effect - when you are transitioning from continuous domain to discrete you have to keep the quantization timing constant in order to get all the frequency information right. Basically, if we don't read the value at regular intervals, we can't apply digital filtering to it. Depending on the frequency content I usually either have automatic ADC sampling set up (implemented differently in different MCUs) which interrupts with a new value on set frequency or just do 
```
if(isTimeToSample()) {
sample()
}
```
in the main loop if sampling is very slow compared to main loop speed.

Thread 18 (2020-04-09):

RespiraWorks/Ventilator #18: Implement communication from Arduino to Pi

neelfirst, 2020-04-09:
Copied thread from inceptionev/FixMoreLungs

@rwilbur: We need to figure out if this is going to use UART or SPI

@lee-matthews: Indeed. Was planning on making possible to set those too. Maybe create some kind of "engineering/debug" mode on the interface module so that we can play with these values directly that's protected from a typical user.

@rwilbur Looking at the clock rate and from what people have said online it appears to be capable of 2Mbps. I agree the differential UART link would be nice to have because of the robustness to noise. I have used RS232 in quite noisy environments and have never had noise issues with it so in practice it might be perfectly acceptable. I think the fewer the parts the better.

@lee-matthews I presume the Arduino only has a UART output (0 to 3.3V) instead of +-12V? To add RS232, we may need to add an extra module anyway, a MAX232 perhaps? Maybe these come in premade modules for rpi / arduino.

@rwilbur I meant 3.3v when I said 232 but that is incorrect. I think the 3.3v UART would probably be fine. The UART on the PI is also 3.3v so they should play nicely together. If these 2 devices are super close together we can probably do a good job keeping noise down by just having a super connection.

neelfirst, 2020-04-11:
Note: for alpha this requires a voltage divider on the Arduino --> RPI line.

derekyerger, 2020-04-11:
I have experienced repeatable reliability issues in high-bandwidth serial comms between a RPi and 32u4-based Arduino platforms. I think this risk is worth mentioning, and should be accounted for in any preliminary testing for component and bus selection.

For low-bandwidth, occasional communication it works fine - I haven't managed to fault isolate but have 3.3v atmel 32u4's directly interfaced to a Pi Zero W for a project and do run into problems sending bursty data between the two.

This problem also spans other Arduino hardware and port choices. For example, SoftwareSerial should probably be avoided, and when used, the baud selection is highly coupled to clock speed.

toybuilder, 2020-04-11:
RPi and Arduino should have no problem communicating via UART at 3v3 CMOS logic-level swing. (As the signaling is internal to the product, we shouldn't need to use RS-232 level swing.)  Assuming the signal is routed properly, there should not be any noise related issues provided that the processors themselves are getting sufficiently clean power.

The "Arduino" needs to be clocked off a crystal/oscillator and not use the RC oscillator.  Provided that both the Pi and Arduino have accurate UART base clock, 2 MHz should be fine, as 2 MHz is an whole multiple of 48 MHz (RPi3), 30 MHz (RPi2) and 16 MHz (Arduino) base clocks.

SoftwareSerial is stupid and should never be used in real-time applications such as this.  Either interface to the hardware UART (i.e. interface through the RX/TX pins at the Atmel and have the USB interface in z-state) or go to a processor with additional UARTs (Mega).

Also, make sure that the Pi has the serial port in raw mode.  If there's any tty handling, it can slurp up data.  And, finally, make sure there is no data overflow.  At higher data arrival rates, there's not much time for the Arduino to work AND handle large amounts of fast incoming data.

Miceuz, 2020-04-12:
I have done RasPi - ATMega328 serial communication before. Having CRCs and frame markers helped a lot as there are still some packets lost from time to time.
It is tempting to have the protocol text-based, this way controller can be controlled directly by connecting to command line over serial - handy when testing. On another hand, maybe having something that has framing over UART makes more sense. Modbus?

martukas, 2020-04-13:
Blocked by #60

Miceuz, 2020-04-13:
BTW, what are bandwidth requirements for this channel? There is just a requirement for pressure display at 25Hz in req document.

lee-matthews, 2020-04-13:
It currently updates at 10Hz, but this can be changed easily.

martukas, 2020-04-23:
This is probably done?

closed 2020-04-23 by jlebar

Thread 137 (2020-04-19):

RespiraWorks/Ventilator #137: HAL test_setAnalogPin improvement

verityRF, 2020-04-19:
**Summary:**
test_setAnalogPin only takes a singular integer as an input. For proper testing needs test_setAnalogPin needs an option to take in an array of integers that will be cycled through for each call. This is because sometimes the analogRead method is called multiple times internal to various controller modules and we need to be able to have it return different values each time it is called during unit/integrated testing. 

**Details:**
Example:
```
int[] myArray = {0, 1, 2};
int myArrayLength = 3;
Hal.test_setAnalogPin(A0, myArray, myArrayLength );
for (int i=0; i<6;  i++) {
printf(stdout, "%d, ", Hal.analogRead(A0));
}
```
would return:
```
0, 1, 2, 0, 1, 2, 
``

**Relevant links:**
[https://github.com/RespiraWorks/VentilatorSoftware/blob/master/controller/lib/hal/hal.h](File In Question)

jlebar, 2020-04-19:
cc @jkff rtyi?

jkff, 2020-04-20:
I thought about something similar - e.g. provide a callback instead of providing a value. Cycling through values of an array could be a special case of that.

However, it has a pretty big problem: the function stops being side-effect-free, e.g. the following two snippets stop being equivalent:

```
x = analogRead(A0);
if (x > 0) return x;
```
vs.
```
if (analogRead(A0) > 0) return analogRead(A0);
```

This may look like a silly example, but code with the same issues (but much harder to find) might appear through several layers of abstraction or through macros. Basically the consequence is that now a test that provides the values for the array needs to know a gritty implementation detail: _exactly_ how many times is `analogRead` called, and in what order.

I was assuming that tests verifying multiple cycles of device operation would work like this:

```
TEST(Foo, Bar) {
  for (int cycle = 0; cycle < N; ++cycle) {
    ...prepare pin values for this cycle...
    device_cycle();
    ...assert that the device behaved correctly this cycle...
  }
}
```

@verityRF Do you think this would be sufficient?

jlebar, 2020-04-20:
Now that I read this closely and understand...

This is exactly what gmock is for.  Instead of having `test_setAnalogPin`, you make analogRead() a mock method, and then you can make it do whatever you want `ON_CALL` -- return the same value, return a series of values, whatever.

jkff, 2020-04-20:
Yeah - but what I'm saying is, I think it's better to leave it as-is, rather than allow mocking it with arbitrary code, because that would encourage people to write tests overly coupled to the implementation and hence both hard to read and fragile, per my example. But it could be that I'm misunderstanding something here, so I'd like to first see an example that seems to require arbitrary mocking.

jlebar, 2020-04-20:
I see now -- I totally agree that would be a too-tightly-coupled test strategy.  analogRead should be side-effect-free.

Sorry for the noise.

verityRF, 2020-04-20:
```
x = analogRead(A0);
if (x > 0) return x;
```

and

```
if (analogRead(A0) > 0) return analogRead(A0);
```
-should- have different behavior, as far as mimicking real controller behavior. In the current case, they are the same, but they shouldn't be. 

The latter means two calls to analogRead, which are separate in time. A time varying real world signal is attached to A0, so if you call that method at time0, you'd get say 1.01 volts, then at time1, a couiple instruction cycles laterr, could be 1.05 volts (depending on the sample rate of the ADC, conversion time, etc.)

I think having a more accurate way of being able to simulate the microcontroller analogRead is important. Yes, it requires the caller to have some idea of how the -test- method is implemented, but that's necessary to enable proper unit testing/integrated testing without hardware involved. This was the purpose of my ArduinoSim module beforehand, which allowed deterministic control over how the analogRead would be simulated from the test modules. 

Again, some modules internally can have multiple calls to analogRead that cannot be exposed in the way you made an example for. 

For instance in sensors.cpp
```
float getPressureReading(int pin, ...) {
float runningSum = 0;
for(int i=0;i<numAvgSamples;i++) {
runningSum += analogRead
}
return runningSum/numAvgSamples;
}
```

In order to test averaging from an external unit test method, I need to preload analogRead via some test method to have different values. This would also hold true if we were to do digital filtering in place inside the loop. 

Now of course, we could decouple the filtering and averaging into intermediate methods, and those can be unit tested individually, but at some point they have to be tied to a method that only contains an analogRead call (as it would be in the real controller code), so how do you do an integrated test on our native machines? 

Options:
1) Having a more accurate analogRead mock for testing purposes
2) Just don't test anything that requires multiple analogRead calls internally, test only the algorithms that attach to them as separate methods by themselves
3) Include a bunch of preprocessor conditionals that get around this on a case-by-case basis (similar to what I was doing with ArduinoSim)

jkff, 2020-04-20:
Thank you for the explanation! This makes sense, especially the getPressureReading example. I agree that this example cannot be adequately handled with the current test_setAnalogPin.

I'm still hesitant to pass an array though - in this example, this will require the caller to know numAvgSamples and to have extra code constructing exactly this many in their array; and we have to worry about potentially going past array bounds.

Could we pass a callback (`std::function<int()>`)? It would allow us to simulate noise here by giving a random number generator; if the caller insists on knowing the exact number of calls, they can declare an array themselves and give `[&i]() { return my_array[i++] }`.

verityRF, 2020-04-20:
Right, I did have a way around this in ArduinoSim by just having an upper length fixed at compile time and the callers can reference that parameter, though that's not ideal either. 

I don't actually care how it's done, wanted your ideas since you guys are more familiar with best practices and gmock itself. As long as we can prime it with a deterministic sequence of data then I'm happy, which I believe registering a callback would allow. This would allow the method to produce what is more reasonable and expected for real hardware operations from a test standpoint.

verityRF, 2020-04-20:
Though I do have concern still about the original example
```
x = analogRead(A0);
if (x > 0) return x;
```
and 
```
if (analogRead(A0) > 0) return analogRead(A0);
```

The fact that those would be the same in the default case for usage of analogRead during test runs concerns me. It sets up the precedent that someone who may not be thinking in a hardware perspective may think those being equivalent is guaranteed, especially since the HAL mock guarantees it, when in reality, it's never guaranteed. 

I don't know what the fix for this might be, if we might even bother with it or just let it go. Would we enforce that you have to register a custom callback just to use it in the first place from the test perspective? That would cause headaches of its own.

jkff, 2020-04-20:
I think having a custom callback be _the only_ API should address your concern. Especially if the function has documentation that clearly explains the issue.

Note: anybody should feel free to take this issue. I'm gonna have less availability during the week during to day job.

jlebar, 2020-04-20:
Is the issue just that we should be introducing noise into the analogRead calls?  Like, instead of saying exactly what analogRead should return, the test harness says "returns a random number with mean X and variance Y" or something like that?

verityRF, 2020-04-20:
The overlying issue is the lack of being able to preload a sequence of data. It could be noise, sure, but it could also be voltages corresponding to pressure waveforms for sensor module testing. It could be voltages corresponding to temperature data for other testing.

jlebar, 2020-04-20:
I guess I am wondering if the following two things can be separated:

1. The desire to have a sequence of data, from
2. The desire to make analogRead() "realistic", addressing the concern in https://github.com/RespiraWorks/VentilatorSoftware/issues/137#issuecomment-616304690 that two subsequent calls to analogRead() should not necessarily return identical data.

I think Eugene and I are pushing back on the notion of "each time you call analogRead() you get a new value from a list" because we've seen this create extremely fragile tests and waste a lot of developer time.  So I was wondering if you thought it would work to say, "up until this point in the test, all calls to analogRead return a noisy number near value X; then, after this point, all calls to analogRead return a noisy number near value Y".

verityRF, 2020-04-20:
I understand the con, but I'm not sure that just having the callback only method causes that much issue, since the developer writing the test knows ahead of time how it would work since they wrote the stimuli. Sure it can cause headache, but I believe you gain from the more robust tests you can perform. It is a tradeoff between test writing concern and being able to do any sort of hardware out of the loop simulation. 

If you two think this is really too bad of an idea, I'll relent. Do look at the attached sensors.cpp (and compare it to the live version in the repo), I want some feedback as to how to unit test the problem that required this discussion (you wouldn't be able to, you'd only depend on the averaging and filtering unit tests, but the zero_sensors() method couldn't be unit tested with how the HAL is written).
[sensors.txt](https://github.com/RespiraWorks/VentilatorSoftware/files/4505775/sensors.txt)

jlebar, 2020-04-20:
> Do look at the attached sensors.cpp (and compare it to the live version in the repo), I want some feedback as to how to unit test the problem that required this discussion (you wouldn't be able to, [...]

What I'm seeing is that to unit test zero_sensors, we want to check that `sensorZeroVals[pin]` is the average of N readings from the pin.

I agree a callback (or even a list of sensor readings) would work for this case.  When we're unit testing sensors.cpp, it's reasonable to expect we know exactly how many calls to analogRead will happen, because we are literally testing that we read from the pin N times.

I actually am not sure if we are in disagreement at this point.  :)  I think a callback as Eugene proposed or a proper gmockable function as I proposed would work fine?  Like, they're both equivalent, in a sense.

jkff, 2020-04-22:
Yeah I'm getting more and more convinced that a callback is the right thing here. As well as providing "write callbacks" for analogWrite and digitalWrite, because as I now understand, in the hardware world write(x);write(y) is not equivalent to write(y) either.

jlebar, 2020-04-23:
Bug ikebana, I'm going to remove the "alpha" milestone because I don't think this blocks the alpha release.  Which shouldn't stop anyone from working on this or anything.

nimamoslemy, 2020-05-01:
Hi, we are a team that needs your feedback to complete our idea.
Please visit our pages and comment on it. 
[github](https://github.com/nimamoslemy/ventilator)
[gitlab](https://gitlab.com/nimamoslemy/avp-ventilator)

jlebar, 2020-05-01:
@nimamoslemy hi, please see https://respira.works/contact if you'd like to engage with us.  Bug trackers are for bugs.

asmodai27, 2022-06-02:
The specific function mentioned in the title have been removed during HAL refactoring, but the point stands: we need a better mock for GPIO, especially analog input pin.

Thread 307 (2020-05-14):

RespiraWorks/Ventilator #307: Need a design for self-test mode

jkff, 2020-05-14:
Per the system requirements (which as of writing can be found [here](https://github.com/RespiraWorks/VentilatorSoftware/wiki/Beta-Milestone#functional-requirements) - see [System requirements](https://drive.google.com/file/d/1HgBBUELFsKxpqV9qQ_b9u50Z6b0gqHHX/view), requirement 131 "Pretest mode"), we must have a pretest mode:

_The ventilator shall have a pre-test mode where the inlet and outlet ports are connected and the  operation of the device is checked including, capability to product correct pressure, function of valves, function of tidal volume measurement._

The existence of this mode raises many questions:
* Should it run on every start-up, or on-demand, or both? 
* Should the device refuse to function until a self-test?
* Should it function only if self-test passes, or can you ignore some errors?
* Should it confirm that you don't have the patient hooked up?
* etc.

**What has to be done**
We need a design for this mode:
* How does it fit into the overall UX of the ventilator
* How is it implemented at a protocol level - i.e. what does the GUI say to the controller, what does the controller say to the GUI.
* It is explicitly OUT OF SCOPE of this design to define which specific self-tests are to be performed. This is just about the protocol and UX; the specific tests will be the subject of a separate issue.

Success criterion:
* the design is written up on wiki (or in the repo) in the form of a Markdown document
* a reasonable person could read the design and confirm that it is in principle capable of supporting at least the tests described in the system requirement
* a good coder could read the design and start implementing it

**How do you know it has to be done**
System requirements say so (see above).

**Code pointers**
As of writing, just `network_protocol.proto` - the protocol will have to be an extension of that.

jkff, 2020-05-24:
Note: This is part of https://github.com/RespiraWorks/VentilatorSoftware/wiki/UI-Requirements.

martukas, 2020-08-07:
Here is an outline posted on May 13th by @inceptionev in #self-test channel (about to be archived around Aug 7)
[original post](https://respiraworks.slack.com/archives/C0135M1BHHD/p1589403525001800)

This is the stub we wrote for Code Life earlier:
1.0 User Procedure
1.1   Power-On Self-Test
At power-on the unit will verify presence and communication between all its internal components, and verify nominal quiescent readings on all its sensors.
1.2   Automated Validation Self-Test
Note: for safety, the Self-Test feature is not available once any patient ventilation program has been selected on the ventilator. The Self-Test is only available after a power-cycle of the unit. The user will tap the Self-Test button on the main screen of the ventilator, which will then prompt the user to connect a standard ventilator hose directly from the inhalation port to the exhalation port. Once the user has confirmed, the unit will automatically proceed with two automated test sequences:
1.2.1 Closed-flow test
For this test, the unit closes the exhaust valve and validates the following:
* Proper blower function
* Proper pressure sensor function
* Respiratory cycle control and timing (PIP, PEEP, RR, I:E)
* Proper exhaust valve function
* No system leaks
* Proper FiO2 function
* Presence and function of the humidification chamber
1.2.2 Open-Flow test
For this test, the unit opens the exhaust valve and validates the following:
* Proper flow sensor function
* Open-circuit detection and alarm
* Proper volume control function (TV)

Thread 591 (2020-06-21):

RespiraWorks/Ventilator #591: BTPS Integration

esc-works, 2020-06-21:
Leaving this here to address later—sorry if I am bad at writing issues. 

BTPS Correction is used to convert flow and volume measured at ambient conditions to the conditions within the lungs. Ambient conditions are called ATP (ambient temperature, pressure); the conditions within the lungs are called BTPS (body temperature, pressure, water vapor saturated).

Currently, the flow measurement and integration does not correct for the fact that the inspiratory flow is generally at atmospheric temperature, pressure, and humidity, while the expiratory flow has been saturated with moisture in the patient as well as increased in temperature. This has not been an issue during prototyping as there is no heat or mass transfer in the test lung. 

The following link describes a standard correction to account for this fact.

https://d3cumwfln92soa.cloudfront.net/8a716ac3fd123ce0becd7b56596582d4fc4c0c47/appnote-btps-correction-v01r.pdf

I believe by my review this can be implemented solely in software without additional instrumentation, but only if the user enters approximate values for altitude and current temperature. We may later want to add sensors, I may make another issue on the hardware side here, as I believe this can be relatively easily (at least, pressure and humidity) accounted for in the circuit board with an additional sensor.

neelfirst, 2020-06-21:
Related HW issue: https://github.com/RespiraWorks/SystemDesign/issues/17

jlebar, 2020-06-21:
> sorry if I am bad at writing issues

This is a fantastic issue.  Thanks, Ethan.

One thing to note, volume zeroing will "fix" this.  The problem is, volume will be off by 10% (if I'm reading this document correctly), and the shape of the volume curve also won't look quite right.

martukas, 2021-01-18:
Related to #652

martukas, 2021-04-07:
We have to way to confirm that our corrections are correct without having humidifier, heater and probably more sophisticated test equipment.

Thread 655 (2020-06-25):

RespiraWorks/Ventilator #655: Proportional valve design tracking.

ebhillstrom, 2020-06-25:
(Editing The original post to have more background - Ethan)
Originally, the flow loop was simple: 
[image]
This worked great in terms of having a simple system. The loop worked by using reserve flow rate capacity to generate backpressure against the tuning valve. This worked, but during inhale, the majority of the flow went out the exhaust. This became an issue when we started to look at Oxygen consumption. The problem is we need to flow oxygen to the patient, at least 30-40% by volume up to 100%. But oxygen isn't a freely available resource, and for patients on high FiO2, we could easily exceed the flow capacity of patient O2 supplies trying to supply high flow rates while wasting most of it. So we decided to include a high-flow solenoid on the exhaust, with a Cv ~4.8 ([flow rate of gallons/minute against 1 psi](http://www.idealvalve.com/pdf/Flow-Calculation-for-Gases.pdf)). This works and is in the current model. The problem is we were using a US Solid solenoid. Asking them repeatedly, they only guarantee 500,000 cycles (a little over 1 day in constant use). We sourced a solenoid from Burkhart for 100,000,000 cycles and its $220, and for the most part seems way overkill for the device.
This is a high flow valve. Specification is as follows:
- Pressure drop: 60 lpm through the valve with a pressure drop of less than 0.49 kpa (nominally a Cv of 2.3).
- Normally open is strongly preferable.
- Pressure is never more than 1.5 psi on either side.
- It needs to open at 0psig (direct lift).
- It doesn't need oxygen cleaning.
- 12V DC

We'd consider two valves in parallel if that was required to get the flow/pressure drop with something in stock.

Three vendors we've tried:

1. Burkhart - pretty helpful. Has sent us free valves. but they are $220 dollars
2. Reinhold automation (MAC valves) - kind of helpful, no free valves, think they misunderstood the spec. 
3. US Solid - Quality/lifetime insufficient. Don't think we can put these in production hardware.

neelfirst, 2020-07-15:
More detailed discussion of pinch valve and anti-asphyxiation brought over from slack (copied and condensed from #658)

- stepper-driven pinch valves are the primary source of pressure control and snap open in the absence of power.
- In a power failure case, both the inspiratory and expiratory valves will open, through which the patient will be able to breathe.
- We will not know until the full loop is built how much resistance there will be.
- Due to this, and the simple design of the pinch valves, it is highly unlikely that a mechanical failure will result either of these valves becoming stuck-closed. The likelihood of both becoming stuck-closed is extremely small.
- This leaves the case in which the valves are actively commanded by the electronics to stay closed. In the event of a computing failure in either the UI Computer or the Cycle Controller, a watchdog timer monitors each and will reset the offending computer, which should then be able to regain control of the valves.
- Furthermore, it will need to be confirmed in the final design that the UI Computer cannot command any modes that will cause the Cycle Controller to hold these valves closed.
- Assuming this is the case, then only the cycle controller needs to be considered in the anti-asphyxiation concept of operations.
- In that case, the Cycle Controller watchdog timer can also be connected to the stepper motor drivers which will default them to an unpowered state in the event of a Cycle Controller computing failure, which will again cause them to snap open, adding another layer of anti-asphyxiation protection

inceptionev, 2020-07-30:
We have concluded to use the stepper-driven pinch valve for blower control and a proportional solenoid (PSOL) for oxygen control.  

TODO to close this ticket:
- Confirm that these updates are reflected in git. (true for pinch valve, confirm for PSOL)

martukas, 2021-01-18:
Testing with this valve has so far been successful. Specific design of mechanical components is superseded by #941

closed 2021-01-18 by martukas

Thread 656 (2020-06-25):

RespiraWorks/Ventilator #656: Selection of overpressure relief valve

neelfirst, 2020-06-25:
On patient inhale side, after O2 mixing, before humidification.

TBD: before or after inhale pressure/flow measurement?

Rafee-UM, 2020-08-03:
From INDIA side we have ordered an over pressure relief valve as per the attached data sheet. Once we got that from the vendor we test it and will update the results. **002-019-1003** is the model which we ordered. 
[SAFETY RELIEF VALVE CATALOGUE.pdf](https://github.com/RespiraWorks/Ventilator/files/5015467/SAFETY.RELIEF.VALVE.CATALOGUE.pdf)

Rafee-UM, 2020-08-03:
As discussed here https://respiraworks.slack.com/archives/C0137BLF17A/p1590440382159500, INDIA team is planning to develop a safety relief valve with help of Umbrella type check valves, which will have absolutely zero leak until the crack pressure is arraived. These are made of medical oxygen compatible elastomer material.
      we are getting the sample quantity of Umbrella valves, once we recieved them, we will revert back with test results. please find the attached umbrella type check valve as your reference. [UM 070.006 SD.PDF](https://github.com/RespiraWorks/Ventilator/files/5015521/UM.070.006.SD.PDF); 
[UM070.006-151.01.pdf](https://github.com/RespiraWorks/Ventilator/files/5015524/UM070.006-151.01.pdf)

inceptionev, 2020-08-30:
Note 2x of Generant VRV-750B-V-0.8-X have been ordered for the US build.  Additionally, two equivalent GRVS units have been ordered for evaluation.  Expected Oct 11th.

Next steps:
- Complete the US enclosed ventilator build
- Compare notes with India build
- Do a complete design review

inceptionev, 2020-08-30:
This comment copied over from duplicate ticket #611 (now closed):
India team has been working on this and selected this valve 002-019-1003: https://respiraworks.slack.com/archives/C0111E2GFPF/p1596284702108100

martukas, 2020-11-04:
Turn out that what we have ordered is actually VRV-250B-V-0.8, which can be decoded using this:
https://www.generant.com/wp-content/uploads/2019/09/SA.SL_.VRV001.G.4514-Series-VRV-Product-Literature.pdf

martukas, 2021-01-06:
The valves have arrived. I think this can be closed for now unless testing reveals the need for an alternative.

martukas, 2021-01-15:
In discussion with @tijanim a problem has been identified that might possibly be a fire hazard. The overpressure valve comes after oxygen mixing and releases the gas into the enclosed ventilator assembly, where electronics reside in the open. In case of 100% oxygen, there may be fire hazards. If this is true, we need to select an "inline" version of the valve, so that we can direct the output to be dumped outside of the ventilator unit.

@jmriphagen @inceptionev @mrkensan  thoughts on this?

inceptionev, 2021-01-15:
Good catch!  Would it make sense to route the patient outlet such that that
the relief valve can be placed outside the unit?  Is there a easily
sourceable inline version of this valve?

inceptionev, 2021-01-15:
Ok, looks like the inline version is just VRVIxxx (with the same parameters)

martukas, 2021-01-28:
Related question -- what pressure should tubing be rated for the relief valve outlet?

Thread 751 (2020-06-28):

RespiraWorks/Ventilator #751: Do not fuse motor

inceptionev, 2020-06-28:
Up for debate: do we fuse the motor?  In some safety critical systems, we do not fuse the most critical component, because it must run no matter what.  I.e. all other fuses exist to protect this component, and fusing it adds a failure point.

dcstraney, 2022-06-23:
Update: On Rev. A, the situation is...
Main power entry and battery have fuses, but 12V to blower doesn't have a fuse.  (Blower motor driver may have a fuse, but that's outside the scope of this.)
Stepper motor drivers also feed from 12V rail - they aren't currently fused but there's a PCB footprint where we could populate fuses to protect the 12V against stepper faults.  Shorts which happen downstream of the stepper drivers (in the steppers themselves or the wiring to them) will be handled by OCP in the L6470.
Other things which feed from VLink, upstream of the 12V power supply, are the 2x 5V power supplies - these aren't fused, but are current-limited (protects against shorts/over-current downstream of these power supplies, but not against failures of the power supplies themselves).

Overall there's two separate power supplies in between the blower and the main DC supply (whether that's from an AC-DC brick, or a battery) with their own complexities, current limits, and many points of failure - so I'm not convinced this discussion is relevant anymore in its current form.  Testing and designing for tolerance to power supply faults at a variety of points in the system is 100% worthwhile, but is its own separate, broader subject as part of a general fault tolerance investigation.

inceptionev, 2022-06-23:
Agreed, this was up for discussion with a previous design effort, but really needs to be part of a comprehensive system-level fault effects evaluation.

dcstraney, 2022-06-24:
Ok, will close this out that as a non-issue, pending a future in-depth fault tolerance investigation.

closed 2022-06-24 by dcstraney

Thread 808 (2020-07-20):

RespiraWorks/Ventilator #808: Add Oxygen Sensor to Controller Code

inceptionev, 2020-07-20:
Basic requirements:
- Analog input similar to pressure sensors, but on pin PC3
- Should have a linear y= m*x + b conversion between counts and an oxygen concentration [0 - 1.0]
- Output should be callable in the same way as the other sensors.

martukas, 2020-07-23:
Someone could help here by finding out which existing code most resembles what is needed.

inceptionev, 2020-07-24:
Oxygen sensor calibration narrative, assuming amplifier gain g_amp and sensor gain g_o2sensor:

- Nominal values:
  - g_amp: 50 V/V
  - g_o2sensor: 0.06 V/fio2 (where fio2 is 0.0 to 1.0)

- Ventilator turns on, starts self-test
- Run blower for 3 seconds with both inhale and exhale valve fully open (and O2 PSOL fully closed) to flush with ambient air.
- Wait at least 10s.  Can run other self-test procedures, but only using ambient air.
- Record the ambient air sensor value in sensors_zero_vals_[FIO2]
- Read the ambient barometric pressure sensor and record the valve (this is not yet supported in hardware, so for now assume 101.3kpa)
- Oxygen concentration output expressed as a 0.0-1.0 value is:
 - std::clamp( (fio2.voltage() - sensors_zero_vals_[FIO2]) * (101.3/p_ambient_kpa/g_amp/g_o2sensor) + 0.21f)

I have started a sample implementation here if it helps, but note that I am not a software engineer, so this definitely needs to be screened for compliance to coding standards and correct implementation.  However a diff between the current master and this branch can help with finding all the places were modifications are needed to add the extra analog channel: https://github.com/RespiraWorks/Ventilator/tree/inceptionev/add_fio2_sensor

inceptionev, 2020-07-27:
Sample implementation in branch https://github.com/RespiraWorks/Ventilator/tree/inceptionev/add_fio2_sensor now includes the scaling

asmodai27, 2020-07-29:
Working on this right now, I have completed the basic framework and adding some unit tests.

I wonder whether we are using the correct correction factor (101.3 / ambient pressure) to go from partial pressure to fraction of volume...
I am not well versed in how that sensor works, but it seems to me that patient pressure should come into play at some point, as the oxygen sensor is seeing patient pressure.
Any insights on this?

inceptionev, 2020-07-29:
Thanks for picking this up.

That's a good point.  The oxygen sensor is an electrochemical cell, so it actually measuring partial pressure of oxygen, not concentration.  It has a sensitivity of 0.00061V/kpaH20_partial_pressure.

While it is true that the sensor is seeing patient pressure, the ambient pressure has a larger effect.  At 10000ft / 305m, there is a drop of 322cmH2O vs sea level, while the max patient pressure is 35cmH2O.  We could take into account patient pressure as well, but we definitely need to make a correction for ambient pressure.

inceptionev, 2020-07-29:
The sensor has a response time on the order of 10 seconds, so I'm not sure how a quickly-changing patient pressure correction would play out.

asmodai27, 2020-07-29:
OK, no problem there.

Regarding the changes in patient pressure, we could approximate the response time with a similar 10 seconds low-pass filter, but without the actual dynamic of the sensor (especially in terms of phase shift), I am not sure of the actual benefits that this would bring. For now, ambient pressure will suffice.

closed 2020-08-12 by martukas

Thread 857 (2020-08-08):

RespiraWorks/Ventilator #857: Design a more flexible system for calibration parameter storage

martukas, 2020-08-08:
**What has to be done**
It should be possible to connect components with different specifications, such as proportional solenoids or sensors, and not have to manually hardcode new calibration/linearization constants and recompile. These parameters should either be stored in non-volatile memory, or could also be set using some combination of convenient pre-compiler flags. 

**How do you know it has to be done**
We now have multiple types of PSOLs that we are testing with, which have different calibration values. We have been forced to hardcode changes. We also have different specs of stepper motors, possibly other components down the line. It would be good to have a more sustainable approach to accommodating different hardware.

asmodai27, 2020-08-08:
The way we do this at my day job is by storing calibration data in specific parameters files, alongside the program. We could use parts of @sglow's hack to write this data at the end of the program memory using the debug interface, or write this to an external EEPROM.
During boot, the program needs to read the file and check its consistency (checksum, values' bounds, ...) before using any value from this file.
Problem with this approach for critical software is we need a way to demonstrate that no possible combination of accepted values can lead to problems inside the software, which is test heavy (could be unit tests though).
A way around that can be to only allow a few specific values instead of a range of values, but this kind of defeats the purpose of such a file.

martukas, 2021-01-18:
Blocked by #712

martukas, 2021-04-07:
Scope:
* PID parameters
* pinch valve constants
* PSOL constants
* venturi constants
* oxygen sensor...

inceptionev, 2021-04-07:
I suspect that the PID values should actually be immutable (hard-coded), as the dynamics of the system should not be different from one ventilator to the next, as long as the actuators and sensors are properly calibrated.  It might even be possible that a real assembly mistake in a production ventilator could be masked by control tuning that essentially compensates for something wrong, like a high resistance or a leak in the system.

martukas, 2021-09-13:
@inceptionev no need for a very formal write-up. Just some ideas on how to most usefully define a "calibration" in the code. For example, for he pinch valve, we may draw the border around this chunk of code:

```
  value = std::clamp(value, 0.0f, 1.0f);

  // Number of intervals defined by the table.
  float tbl_len = static_cast<float>(calibration_.data.size() - 1);

  // Convert the input value based on a table
  // used to linearize the pinch valve output
  int n = static_cast<int>(value * tbl_len);
  float f = value * tbl_len - static_cast<float>(n);

  if (n == static_cast<int>(tbl_len))
    value = calibration_.data[n];
  else
    value = calibration_.data[n] + f * (calibration_.data[n + 1] - calibration_.data[n]);

  // Convert the value to an absolute position in deg
  // The motor's zero position is at the home offset
  // which corresponds to fully open (i.e. 100% flow)
  // The valve is closed at a position of -MaxMove;
  float pos = (value - 1.0f) * MaxMove;
```

where `value` is mapped to `pos`. This would define a relationship between %volumetric flow vs. stepper angular position. But the question is, do we want the clamp as part of the abstraction?

Other use cases would be:
PSOL -- would it map flow vs. voltage? Also clamp?
Blower -- any nonlinearity to deal with there? What are the input and output units?
Sensor abstractions already map ADC voltage to appropriate units, but is this adequate? Any nonlinearity to deal with there?

Does it even make sense to have a similar implementation for all these cases? If these functions are sometimes represented by a polynomial mathematical operation, even if it is "good enough", is it still most robustly represented by an empirically constructed curve?

I will very likely first refactor the pinch valve, but it would be good to already make something that could be reused to the benefit of other parts.

martukas, 2021-09-13:
Other related tickets:
* #870 
* #838 
* #633 
* #170

inceptionev, 2021-09-26:
I have a strong preference for all actuators (PSOL, pinch valve, blower) to be mapped from 0.0 to 1.0, zero being fully closed, and 1 being fully open.  The calibration ideally would be such that an input from 0 to 1 yields a linear response in flow through the valve.  This makes control easier.

Clamping should be included in the calibration (both PSOL and pinch valve) and should be such that 0 is the lowest point at which further negative motion does not result in a reduction of flow, and 1.0 is the highest point at which further positive motion does not result in an increase of flow.

For the blower, we don't do any closed loop control around this yet, so it's not necessary at this point.  However, having the capability to assign a calibration curve to the blower would be a nice-to-have, in case we do add control in the future.  For now, if we implement blower calibration, we can just set it to 1:1 for now.

I think it makes sense to have all of these use the same calibration system.  The pinch valve uses an 11-point calibration, right?  we could apply that to all the actuators.

The sensors are a bit trickier.

- Venturi has a polynomial conversion.  If the 11-point calibration could sufficiently capture this polynomial curve, we could convert it over to using the interpolated 11-point system.  This would also make it easier to empirically calibrate.  I would say, keep this as is for now, but let's experiment with this once we have a setup that can physically calibrate the venturis.
- Oxygen sensor: we'll only be able to do a 2-point calibration since we can only test at 21% and 100% oxygen, but that is no reason we can't represent this as the same 11-point interpolated calibration, so it makes sense to make the oxygen sensor use this calibration as well.  The 11 points will just be linear interpolations between the two points, extending down to 0% and up to 100%.  This is OK because galvanic oxygen sensors are very linear, even as they age.  The error they gain with age is an offset.

closed 2022-06-02 by asmodai27

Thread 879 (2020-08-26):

RespiraWorks/Ventilator #879: Dear Team, we are using MPX5700AP/GP/GP1 CASE 867B-04 gauge pressure sensor in the oxygen line we think to use PC2, PC3 pins cycle controller we have a doubt that in the existing circuit we are using a scaling circuit. please suggest whether the same scaling, the filter circuit can be used for the gas sensor or not please suggest if any modifications required Thank you.

saipraveenpanchakarla, 2020-08-26:
Please take the time to describe the bug in detail, so other contributors can pick it up and implement or declare done/obsolete in case it was fixed out of band.

**Current behaviour**
* Describe what is wrong with the system as of writing: what is the actual state of things.
* Instructions to reproduce the bug.
* Screenshots, screencasts, or video to help explain your problem.

**Expected behaviour**
* Describe what is the expected state of things.
* Identify documents that need to be updated, especially in case of hardware component choices or changes assembly.

**How do you know it is wrong**

Link any documents, Slack threads, quote personal communication, reference your personal domain expertise etc. explaining why you think the current state of things is bad and the expected state of things is good.

**Code pointers**

Give some thoughts on roughly where in code do you think the necessary changes might be located.

**Don't forget**
- [ ] Put the issue in a milestone
- [ ] Assign it to one of the projects
- [ ] Add appropriate labels
- [ ] Mention dependent/blocked issues if any

saipraveenpanchakarla, 2020-08-26:
Dear Team, we are using MPX5700AP/GP/GP1
CASE 867B-04 gauge pressure sensor in the oxygen line we think to use PC2, PC3 pins cycle controller we have a doubt that in the existing circuit we are using a scaling circuit. please suggest whether the same scaling, the filter circuit can be used for the gas sensor or not please suggest if any modifications required Thank you.

martukas, 2020-08-26:
Duplicated following the proper template in #880

closed 2020-08-26 by martukas

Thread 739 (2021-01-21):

### ISSUE TITLE
Rev 1.0 PCB: DNP components are stuffed

### ISSUE THREAD

**Issue by inceptionev** [RespiraWorks/Ventilator#739]
@sglow discovered 5V on the CC-3V3 rail. Looks like this is because JLCPCB stuffed many of the DNP components in the BOM. Fix: remove R2, R73, R75, R77. R67, R17, R18, R59, R60, R68, R69

**Comment by dcstraney** [comment]
No longer relevant to "clean start design" for Rev. A; will be careful about DNP markers in BOM.

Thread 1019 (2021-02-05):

RespiraWorks/Ventilator #1019: More custom tubing fittings

martukas, 2021-02-05:
**What has to be done**
There are multiple combinations of McMaster fittings that can be replaced by custom 3d printed parts. In particular:
* oxygen sensor +overpressure valve manifold needs one more twist on the end, towards the filter face
* exhale return has 2 elbows in sequence
* exhaust output path has 2 elbows in sequence

**How do you know it has to be done**
This **maybe** has to be done, but maybe not?

[image]

There is not enough vertical space under pneumatics panel for 2 elbow fittings to go end-to-end. This makes installing difficult.
It could be that in the next iteration we will have more space under the acrylic and these custom parts will not be necessary. 
However, it might be overkill to modify metal enclosure design to accommodate plastic. However, the space under the pneumatics tray might still be increased due to other more salient reasons, for example -- space for backup battery.
However, there are still advantages to doing custom fittings - fewer assembly components means fewer failure points; plastic is easy to get manufactured to spec and there is practically no advantage to using the McMaster fittings past the initial prototyping stage.

**Code pointers**
Should make sure you are working with the latest pneumatic assembly to get an idea for the sizing of these parts. Vertical distance should be easy to measure in the assembly.
The fittings can be shorter than the maximum constrained, just like the blower adapter, for example.

There can be a new directory and page under pneumatics for "custom tube fittings", which could have the whole lot of them in there, instead of making separate pages for each. 

**Don't forget**
- [ ] Put the issue in a milestone
- [ ] Assign it to one of the projects
- [ ] Add appropriate labels
- [ ] Mention dependent/blocked issues if any

tijanim, 2021-02-06:
Thinking simbple 3-d print u-fittings will work. We may need to expand the thru hole slightly to allow them to snake thru, but shouldn't be an issue

martukas, 2022-06-20:
This is awaiting a merge in #1038 . The branch may be taken over by a new contributor and merged. Though likely these components will change yet again before v0.4 is completed.

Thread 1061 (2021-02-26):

RespiraWorks/Ventilator #1061: Power loss alarm battery (AA) compartment selection

martukas, 2021-02-26:
**What has to be done**
There is an alarm for power loss that is autonomous and is powered by some AA batteries. These may have to be occasionally replaced. There should probably be an easily accessible compartment for these batteries on the back of the ventilator unit, and this compartment should be wired to the PCB.

We need to select this part so that we know how much space to provision for it in the enclosure and back acrylic panel. We need to do this prior to V0.4 enclosure design, so that we can:
* make sure it fits next to the PCB on the back panel
* make sure the opening in the sheet metal closure panel is big enough for this component among others

**Don't forget**
- [ ] Put the issue in a milestone
- [ ] Assign it to one of the projects
- [ ] Add appropriate labels
- [ ] Mention dependent/blocked issues if any

dcstraney, 2021-02-27:
Both the Keystone 2478 (http://www.keyelco.com/product-pdf.cfm?p=1040) and MPD BC4AAW (http://www.memoryprotectiondevices.com/datasheets/BC4AAW-datasheet.pdf) have a very common form factor and are available from multiple distributors.  Only thing to watch out for is the slightly different mounting hole spacings; Keystone's are countersunk and meant to use flat-head screws while MPD's are out of the direct path of the batteries and likely meant for some fairly low-profile such as pan heads.

martukas, 2021-03-25:
This has also been suggested:
https://complete-electronics.com/manufacturers/bulgin/battery-holders/bx0027bx0027

dcstraney, 2022-06-23:
Let's settle on the BX0027 for the foreseeable future, as the panel-mount "pull-out" form factor is really convenient?  (The other "classic" 4x AA form-factor ones can be the backup option, as those are easier to find swappable equivalents for, with a bit of thought to the mounting hole pattern)  It's currently available in reasonable-to-excellent quantities from a variety of distributors, so this isn't some hard to find, rarely-in-stock part.

martukas, 2022-11-10:
According to clearance holes in spec, mounting this would require m3
* measured mounting tab thickness = 2.4mm
* acrylic thickness = 6.35mm
* locknut = 4mm
* (optional 9mm OD washer = 0.8mm)

This totals 12.75-13.55mm. Therefore, mounting screws should be about 14mm.
Proposing this: https://www.mcmaster.com/92125A133/

martukas, 2022-11-10:
Locknut: https://www.mcmaster.com/93625A100/

closed 2023-03-21 by martukas

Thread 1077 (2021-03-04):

RespiraWorks/Ventilator #1077: Ventilator PCB Rev A Schematic Design Review

inceptionev, 2021-03-04:
This purpose of this ticket is to record and discuss the schematic design review of the Ventilator PCB Rev A.

We've split the pages up between engineers and this ticket can serve as a checklist.  If there is a finding that results in more than a minor or formatting change, please create a separate issue ticket for it and link it here.

- [ ] TOP (Stephanie)
- [ ] Logic/Control Power Supplies (Edwin)
- [ ] 5V UI/ / Control Supply (Edwin)
- [ ] 3.3V Logic / Sensor Supply (Edwin)
- [ ] Cycle Controller (Don)
- [ ] UI Computer (Edwin)
- [ ] Alarms and Power Monitoring (Stephanie)
- [ ] Indicators (Edwin)
- [ ] Safety FPGA (Edwin)
- [ ] Pressure Sensors (Stephanie)
- [ ] Pressure Sensor Daughterboard (Stephanie)
- [ ] Oxygen and Temperature Sensors (Don)
- [ ] NTC Temp Sensor (Don)
- [ ] Stepper Motor Driver (Edwin)
- [ ] Additional Aux Functions (Stephanie)
- [ ] System Monitor / FPGA ADC (Stephanie)
- [ ] Power Entry / Battery Handling (Don)
- [ ] Battery Charger / Source Switching (Don)
- [ ] Battery Balancer (Don)
- [ ] 12V System Buck Converter (Don)
- [ ] PSOL / Heater Driver (Edwin)
- [ ] STM Programmer for Cycle Controller (Stephanie)

We want to have a comprehensive design review before we go into layout.

Here are the original board requirements: https://docs.google.com/document/d/1RPkyGj1lCVv08fhpkGO5IUJaUcc130k_tNvB63ljrs0/edit?usp=sharing

Here's a schematic review checklist as a guideline, feel free to add to this:
- [ ] Transistors, diodes, and polarized caps oriented correctly.
- [ ] Pinout checks for all components
- [ ] Capacitor voltage ratings and voltage-capacitance derating
- [ ] Thermal margin for power components (see ticket 
- [ ] I2C nets not swapped and with one set of pullups, somewhere (remember that some modules like the RPi have onboard ones)
- [ ] MISO/MOSI directions and daisy-chaining, if applicable.
- [ ] JTAG direction and daisy-chaining, if applicable
- [ ] Single pin nets (apply NC / NoDRC mark if applicable)
- [ ] Input-output directions on ports and components
- [ ] Check for misspelled or incorrect power rail names
- [ ] Title block correctly filled out

**Don't forget**
- [ ] Put the issue in a milestone
- [ ] Assign it to one of the projects
- [ ] Add appropriate labels
- [ ] Mention dependent/blocked issues if any

inceptionev, 2021-03-05:
Potential changes in **bold**, everything else is just comments

**UI Computer:**
- Pinout check is good.
- **Doesn't look like +5V_RPi connects to anything (upper left of TOP sheet).  Should this be +5V_GUI?**
- **We've had trouble with powering the touchscreen exclusively from the pi's USB ports in the past, we should add a 2-pin micro-fit connector to provide 5V to the touchscreen independent of the Pi**
- **Let's flip the bit on UI_ID0 from 0 to 1.  The ID is meant to tell the software which version PCB it is plugged into, and 0b00 was rev 1.0.  Same goes for the Cycle Controller.**
- **Do we have a receptacle to receive the USB UART adapter TX/RX? (or are we even using it anymore? We wanted to have the Rpi be able to program the Cycle Controller, but can that be done through the STLink?)**
- **I think we might want the buzzer on one of the PWM pins**
- **The Rpi 3B+ never had well-published alternate pin functions, so we used generic GPIOs for CTS/RTS on PCB Rev 1,0, but the Rpi 4 does, [here](https://www.raspberrypi.org/documentation/hardware/raspberrypi/bcm2711/rpi_DATA_2711_1p0_preliminary.pdf), and it has dedicated UART0 CTS and RTS lines. CTS0 and RTS0 are on GPIO 16 and 17, respectively.**

inceptionev, 2021-03-05:
**Logic/Control Power Supplies**
- [x] General design looks good
- [ ] **CSD17304Q3 on 5V-USB-En: this should be a P-Ch FET for this work, also this is pretty oversized for the circuit, and we might be able to eliminate the level-shifter if we used a smaller, logic-level PFET (MTM231232LBF in SC70 package would do the trick.  Even better, I suspect we can lose this circuit altogether as we have been using the current Nucleo board with JP5 in the E5V position, and so this circuit was never exercised, and we had no troubles with programming.  Maybe leave the 5V-USB to diode-or into 5V-Ctrl so we have the option of powering the STLINK/CC/Sensors section of the board from USB when it is detached from the vent.**

**5V Buck Converter**
- [x] Pin check is good
- [ ] **Power Good is an open drain signal, so the testpoint won't have much meaning without a pullup**
- [ ] Inductor does not have a part selection so can't check power yet.
- [x] Diode: worst case with ambient at 40C, 70% duty cycle (16.8V VLink), diode Tjmax is 150C, and Rthja of 85C/W gives about 1.3W capability, which at Vf of 0.4V and duty cycle of 70% is 4.6A.
- [ ] **At Vlink of 16.8V, the 7.2uH inductor will give a ripple current of 1.2A, which feels high for our likely consumption of 2A on UI and <1A on CC.  10uH might be better.**
- [x] FB resistor divider yields 4.98V
- [x] Cap voltages on defined caps look good, but **100nF cap is not defined**

**3.3V LDO**
- [x] Pin check good
- [x] Cap voltages good
- [x] Power good in this case is a driven output, so is fine without a pullup

inceptionev, 2021-03-05:
**General**
- [ ] What, if anything, do we do about the battery charger needing a host to set charge current?  Won't charge the first time it is plugged in.
- [ ] Can we rename net oxygen level to oxygen_concentration or oxygen_fio2?  I feel like oxygen level makes it sound like a tank level.

inceptionev, 2021-03-05:
**Safety FPGA**

- [x] Pin check good
- [x] I2C polarity and pullups good

inceptionev, 2021-03-05:
**Indicators**

- [x] Simple page.  everything looks good here.  
- [ ] Not sure we need two power pins for 5V and GND, each of those microfit pins can carry 8+A.  Was the 10-pin connector selected to make it dissimilar from the other connectors (to avoid mistaken mating)?

dcstraney, 2021-03-05:
UI Computer:
- Touchscreen power: makes sense, done
- ID bits: same, for RPi.  **For the cycle controller I don't see any ID bits though, looks like it was never assigned in the ICD.  We may have to ditch the SD card to free up pins for this.**
- **Receptacle for USB UART: I don't know much about this - the STLink does have its own tx and rx but I couldn't find any info in the STLink manual about whether it exposes that as a generic USB serial interface.  Wouldn't hurt to have an extra connector for that.  Any preferred USB-serial cable? (I like the FTDI TTL-232R-3V3 personally but don't know if you guys already have a specific one on-hand)**
- Buzzer on PWM: yep makes sense, I noticed it wasn't when looking at the ICD but figured it was for a reason/holdover from last version. GPIO18/19 can also host PWM0/1 but with GPIO12/13 being freed up below...
- RTS/CTS: good find, changed.

Logic/Control Power Supplies:
- 5V-USB-En: Oops, I meant to copy over one of the P-FETs from the battery controller, looks like I grabbed the wrong one. (And yeah it's oversized, but didn't seem worth finding then sourcing an extra part for a one-off; same with the level-shifter even though it would be overcomplicating things in a different design; already had one for the blower)  Even better though if we can just ditch the power-switching bit though.  Yeah the point of the diode-OR is to be able to program the STM without powering up the whole thing, it was in our initial spec I think.
5V Buck:
- Power Good: yeah it's not actually intended for probing, it's just a "just-in-case" testpoint so in the rare event we actually need a power-good signal it won't be as hard as soldering to a DFN pin - figured we'd patch in a pull-up if we do happen to actually want to use it.
- Inductor: sounds reasonable, I just took that from the existing design, will use one in the same series as one of our existing ones.
- 100nF cap: not all the cap voltages are defined yet, that's still in process; I haven't picked out the USB mini-B connector yet either for the STM programmer.

General:
- Oxygen: sure, oxygen-FiO2 sounds reasonable (...-concentration seems overly long for typing out labels); changed.
- Pi power: good catch, fixed.  Deleted +5V_Rpi from library to prevent future mixups.

Indicators:
- Doubled pins: I agree we don't need 2x, will leave Stephanie to answer about the dissimilar pin #?

inceptionev, 2021-03-05:
**Actions from meeting:**
- [ ] Switch valve driver fuse to PTC
- [ ] Check in with software about how to do RPi to STM32 programming
- [ ] Switch to 100-pin version of STM32

inceptionev, 2021-03-06:
**PSOL Driver**

- [ ] **recommend enlarging lower FET bypass 0Ohm resistor to 0805 or bigger, to carry to up 2A.  Same with the high-side bypass 0Ohm resistor.**
- [ ] **recommend making the fuse a thermally resettable one, 0ZCF0200AF2C was selected for Rev 1.0**
- [x] cap voltage good
- [x] thermal: worst case Rds(on) @150C of 166mOhm, ambient temp of 40C, Rthja of 41C/W, yields max Pdiss of 2.7W, which equates to 4A of current.
- [x] pin check good
- [x] current limits and current sense resistor calculations good
- [ ] **Should we consider a resistor divider instead of the 10k current limiting resistor for the CS output?  Even weak overvoltages can saturate an ADC and affect the next reading in the conversion.**

dcstraney, 2021-03-07:
All sound reasonable; implemented.

dcstraney, 2021-03-07:
Changed the NTC temp sensor slightly to put the ESD protection on both pins just in case (might as well since one side was unused).  Can revert if there's a reason not to do this.

stephmusinsky, 2021-03-07:
swapping UI LED pinouts on ICD to match top level (just with each other)

stephmusinsky, 2021-03-07:
Pressure Sensor page: 
BMP280 symbol missing pin 7 to ground

stephmusinsky, 2021-03-07:
Additional Aux:
Found the I2C pull-ups I didn't see originally for CC-SDA/CC-SCL. I vote to leave on top page and take out here

stephmusinsky, 2021-03-07:
System Monitor ADC:
LM4120 symbol wrong: 5 should be labeled VOUT, but okay connections. Pin 1 named VRef (would be good to show it unconnected)

dcstraney, 2021-03-07:
All good catches, fixed

stephmusinsky, 2021-03-07:
STM Programmer:
Two pins have CC_SWCLK_OUT

dcstraney, 2021-03-07:
That's correct actually, it follows the nucleo STLink schematic (which is a massive pain to read because it's under-documented and has terrible net naming, but that's a separate story).

inceptionev, 2021-03-08:
**Stepper driver**

- [ ] pin check: everything correct, except symbol name is EPAD, but footprint name is 37.  Recommend fix this on the footprint.
- [x] IO wiring, LEDs, daisy-chain, all look good
- [x] Power wiring good
- [x] Cap voltages good

inceptionev, 2021-03-08:
Review things:

- [ ] Swap the indicators connector to 8 pin
- [ ] DNP the i2c pullup resistors on the FPGA page (the module has them already)
- [ ] check that the TVS diode on the NTC thermistor is correct
- [ ]

dcstraney, 2021-03-08:
From the first pass of thermal calcs it looks like the FETs can be made to work, but the DC (BATFET, Vin-Adp switches, Pack-P battery balancer switches) and buck high-side FETs (battery charger, +12V supply) definitely need some real heatsinking.  The buck low-side FETs are fine with the minimal footprint because duty cycles are always pretty high.  Any heatsinking scheme that gives a total Rth-ja of 70 K/W or less should work well for everything: can either...
1. Add lots of copper area, mechanical engineers probably won't be the biggest fan of this one but it might not be that bad space-wise
2. Via down and put a metal plate against the bottom of the board through some gap pad for electrical isolation
3. Use some SMT heatsinks like these guys: https://octopart.com/search?q=573100d00010g

inceptionev, 2021-03-08:
I'll take a look and see if we can find some lower Rds(on) options.  These aren't switching FETs so we don't care as much about Qg.  Might add BOM lines, but I think that is better than adding assembly steps.

inceptionev, 2021-03-09:
@dcstraney do you have your thermal calcs written down somewhere?  The only part I'm getting in my calcs as marginal is the P-Ch BATFET in the BQ24773 circuit, which we can definitely solve in the BOM by going to a 5x6mm part with lower thermal resistance and a bit less Rds(on).  Using the datasheet thermal resistance to ambient, with thermal vias to a backside ground plane, and a 35C ambient temperature, I get a temperature margin of 20C.  Not great, and we can get to a much better margin of 98C by going to SI7145DP-T1-GE3 (a 5x6 part).

All other parts have at least 30C of temperature margin mounted to the board with a solid backside ground plane and thermal vias as the only heatsinking.  The worst one is the BQ24773 because of its high switching frequency, and we are doing about as well as we can in the 5x6mm part class.  We do have the option to improve this by lowering the switching frequency from the default via i2c.

The DC FETs on the AC input have 44C of thermal margin.  I think that's good as I don't see our adapter current going up past the 120W level.

LM5141 switching FET has 53C of margin, and that's probably fine.  We could go up to a 100W blower and still be ok.  Lie you said, the bottom side FET is fine, because it's basically never on.

The FETs on the MAX17320 battery protector/balancer have 39C of margin.  This should be fine as-is, but we can open up the option for higher power blowers by going to a 5x6mm package here.

Calcs are here: https://docs.google.com/spreadsheets/d/1Otu4uRq1WR7CHx7AOSxF2eoAqoWKeeAT3UDNmPhiSdw/edit?usp=sharing

I'll get these changes (BQ24773 PFET and MAX17320 NFETs) into the schem shortly.

dcstraney, 2021-03-09:
Yeah, I took notes in a text file; it's the kind of thing that makes perfect sense to me but would be an embarrassing mess to anyone else so was going to check it against / put numbers into the spreadsheet later when I got a chance.
Anyways it looks like the main difference I can see is the different Rds-on values we're using - I'm using the max. values, plus accounting for the increase in Rds-on with temperature.  For the high-side buck CSD18563 for example the spreadsheet has 8.6 mOhms, or 10.8 mOhms max., but those datasheet values (for Vgs=4.5V) are at 25 C.  From figure 8 in the datasheet there's a ~1.6x multiplier @ 125 C, so if the final result does end up with Tj ~= 125 C then the real Rds-on is more like 17 mOhms.

inceptionev, 2021-04-21:
Review complete, design submitted.  Closing ticket.

PR #1101 (2021-04-26): Ventilator PCB Rev A
# Description

This is the design and layout of the Rev A PCB done on branch pcb_block_layout by @dcstraney, @stephmusinsky, and @inceptionev.  This design was reviewed on #1077 and layout completed on #1081 

Closes #1077 
Closes #1081
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

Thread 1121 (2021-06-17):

RespiraWorks/Ventilator #1121: Pinch valve rotor press-fit has play

martukas, 2021-06-17:
**Current behaviour/situation**
Pinch valve rotor slides on too easily onto the stepper D-cut shaft and wobbles. Behaviour can be reproduced when printing with a relatively dimensionally stable resin such as Siraya Build or Siraya Fast. In this particular case, the rotors were printed vertical, but likely would still be an issue printed in other orientations.

The reason this problem may not have been seen before is that when printing the rotor vertical without supports, the bottom surface that is on the build plate will experrience some bloom due to increased exposure time on the first few layers. This will create a tighter fit when first inserting. However, the rest of the shaft interface is nevertheless too wide/loose. If exposure compensation is used for the bottom layers, or rotor is printed with scaffolding rather than directly on the build plate, or rotor is printed in another orientation, the problem will become apartent.

**Expected state/behaviour**
Rotor press-fit should be tight throughout the entire length.
Pinch valve Inventor models should be updated as well exported step files.

**How do you know it is wrong**

If the rotor is not well fit to the stepper shaft, it will wobble in operation and:
* calibration/linearization may not hold
* closed loop control behavior may become unstable
* rotor component may experience damage from repeated stress and eventually become even more loose, likely making the valve inoperable

**Starting points**
Should use manufacturer datasheet AND measure the shaft carefully with calipers. Should test print a few times to confirm that the dimensions ensure a tight fit.

**Don't forget**
- [ ] Put the issue in a milestone
- [ ] Assign it to one of the projects
- [ ] Add appropriate labels
- [ ] Mention dependent/blocked issues if any

martukas, 2022-01-22:
As of Summer 2021 this is still not solved. Might be 3d printer resolution limitations rather than design issues - i.e. would require a manufacturing method with better tolerances or perhaps reintroduction of set screw to stabilize the fit.

inceptionev, 2022-11-21:
This is probably a printing issue.  In the rotors we had printed for earlier units, it is tight all along the shaft and there is no wobble.  We also fitted the rotors on the shaft before post-curing, then cured the rotors while on the shafts.

I think we can solve this by adding these printing specifics to the documentation so that we get repeatable results.  For most other parts this is probably not needed, but for pressfit parts it may be necessary.

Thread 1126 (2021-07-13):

RespiraWorks/Ventilator #1126: PEM Nuts on acrylic is hard to assemble

gokcemay, 2021-07-13:
Please take the time to describe the issue in detail, so that other contributors can pick it up and implement or declare it done/obsolete in case it was fixed out of band.

**Current behaviour/situation**
* There are 6 PEM nuts on acrylic tray. These are fixed to internal tray. However tolerance buildup is an issue. Some bolts can't be assembeled.
* One way to fix it is to measure locations before cutting acrylic and fixing PEM nuts. 
* Another way to fix it is to increase hole sizes on internal tray. An increase to 5mm diameter might be enough.

**Expected state/behaviour**
* In order to change internal tray CAD files should be updated.

**How do you know it is wrong**

I tried to assemble it and found that there is a problem. Tighter production tolerances might solve the issue.

Link to requirements or risk analysis if applicable.

**Starting points**
Check tolerance buildup. What is the maximum issue we might have?

**Don't forget**
- [x] Put the issue in a milestone
- [x] Assign it to one of the projects
- [x] Add appropriate labels
- [x] Mention dependent/blocked issues if any

martukas, 2021-07-20:
Increasing hole sizes seems reasonable.

martukas, 2021-09-27:
Implemented in #1159

PR #1159 (2021-09-27): Equipment tray pem nut locations
# Description

This PR closes two issues. 
* One is because of tolerance build-up possibility 6 holes on the pneumatic tray might not align with the ones on equipment tray. Thus we need to increase hole sizes to ease alignment. That is done and holes on acrylic pneumatics tray are 1mm bigger in diameter. 
* The second issue was assembling and disassembling pneumatics tray was difficult. Bolts fit from bottom. Heat fitted nuts on acrylic were removed and PEM nuts are fitted to equipment tray to solve that issue. However M4x8mm bolts were short so 10mm in length  [... cut]
closed 2021-09-27 by martukas

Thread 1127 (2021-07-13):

RespiraWorks/Ventilator #1127: Nuts on acrylic is hard to assemble and dissasamble

gokcemay, 2021-07-13:
Please take the time to describe the issue in detail, so that other contributors can pick it up and implement or declare it done/obsolete in case it was fixed out of band.

**Current behaviour/situation**
* Acrylic panel has to be assembled and disassembled a few times to test the build. They are on acrylic, thus bolts have to be inserted from under the internal tray. There isn't a lot of space there.

**Expected state/behaviour**
* Acrylic and internal tray CAD files

**How do you know it is wrong**

Assembling the enclosure and tray showed it is hard to dis/assemble.

Link to requirements or risk analysis if applicable.

**Starting points**
A solution is to move nuts to internal tray. Another solution is to use the design as it is but put bolts from top. Thus use those bolts as indexing pins.

**Don't forget**
- [x] Put the issue in a milestone
- [x] Assign it to one of the projects
- [x] Add appropriate labels
- [x] Mention dependent/blocked issues if any

martukas, 2021-07-20:
Not totally clear on which ones are the problem. Can we have some pictures to illustrate?

martukas, 2021-09-27:
Implemented in #1159

PR #1159 (2021-09-27): Equipment tray pem nut locations
# Description

This PR closes two issues. 
* One is because of tolerance build-up possibility 6 holes on the pneumatic tray might not align with the ones on equipment tray. Thus we need to increase hole sizes to ease alignment. That is done and holes on acrylic pneumatics tray are 1mm bigger in diameter. 
* The second issue was assembling and disassembling pneumatics tray was difficult. Bolts fit from bottom. Heat fitted nuts on acrylic were removed and PEM nuts are fitted to equipment tray to solve that issue. However M4x8mm bolts were short so 10mm in length  [... cut]
closed 2021-09-27 by martukas

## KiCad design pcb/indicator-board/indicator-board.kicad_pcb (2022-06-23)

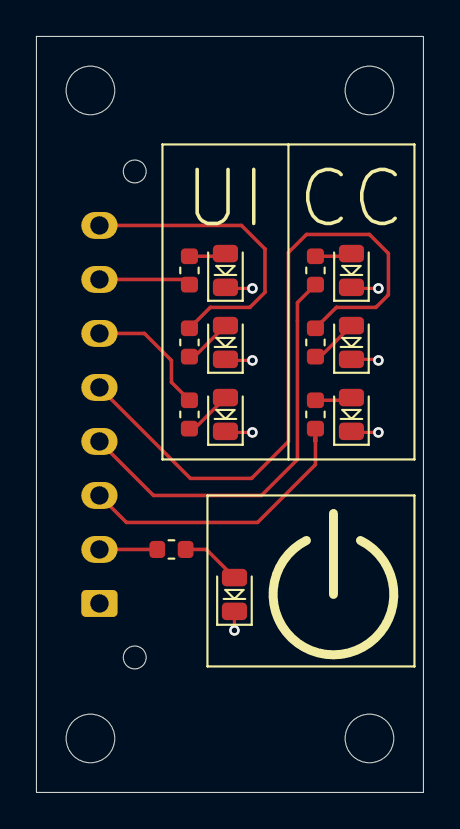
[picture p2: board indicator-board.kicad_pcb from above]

Board: 4 copper layers, 21.5 x 42.0 mm, 19 parts (1 on the bottom side), 15 nets.

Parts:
D1, D2, D5: Green; LED_0805_2012Metric
D3, D6: Yellow; LED_0805_2012Metric
D4, D7: Red; LED_0805_2012Metric
H1, H2, H3, H4: M2.5; MountingHole_2.7mm
J1: Cable to from main board; Molex_Micro-Fit_3.0_43650-0815_1x08_P3.00mm_Vertical
R1, R2, R3, R4, R5, R6, R7: 1k; R_0603_1608Metric

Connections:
+5V: J1.2, R1.1
/CC-LED-G: J1.3, R2.1
/CC-LED-R: J1.4, R4.1
/CC-LED-Y: J1.5, R3.1
/UI-LED-G: J1.6, R5.1
/UI-LED-R: J1.7, R7.1
/UI-LED-Y: J1.8, R6.1
GND: D1.1, D2.1, D3.1, D4.1, D5.1, D6.1, D7.1, J1.1
unnamed: D1.2, R1.2
unnamed: D2.2, R2.2
unnamed: D3.2, R3.2
unnamed: D4.2, R4.2
unnamed: D5.2, R5.2
unnamed: D6.2, R6.2
unnamed: D7.2, R7.2

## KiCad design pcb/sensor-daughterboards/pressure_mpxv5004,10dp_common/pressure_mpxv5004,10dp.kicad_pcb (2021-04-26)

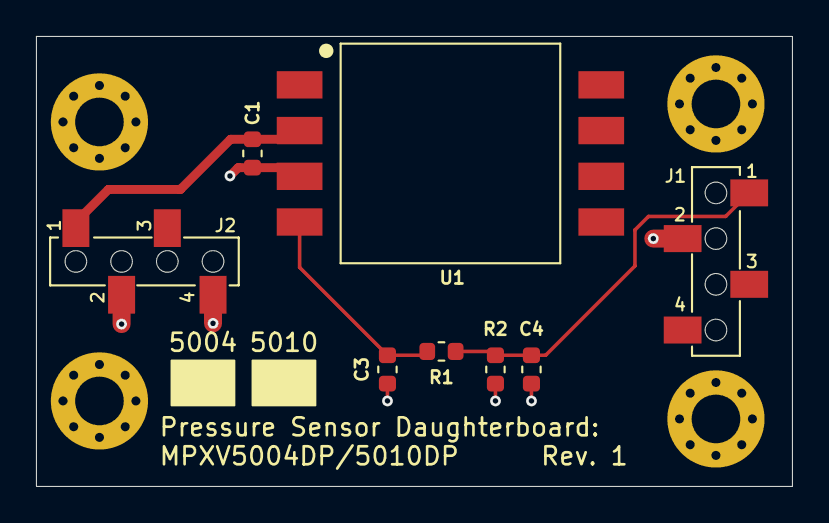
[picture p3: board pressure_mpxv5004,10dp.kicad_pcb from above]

Board: 2 copper layers, 42.0 x 25.0 mm, 12 parts (0 on the bottom side), 4 nets.

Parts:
C1, C4: 1uF; C_0603_1608Metric
C3: 470pF; C_0603_1608Metric
H1, H2, H3, H4: M2.5; MountingHole_2.7mm_M2.5_Pad_Via
J1, J2: Main board connections (bottom entry); PinSocket_1x04_P2.54mm_Vertical_SMD_TE_1241152-4
R1: 2.4K; R_0603_1608Metric
R2: 4.7K; R_0603_1608Metric
U1: MPXV5004DP; NXP_MPXV5004DP

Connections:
+5V_Sns: C1.2, J2.1, U1.2
GND: C1.1, C3.1, C4.1, J1.2, J2.2, J2.4, R2.1, U1.3
unnamed: C3.2, R1.2, U1.4
unnamed: C4.2, J1.1, R1.1, R2.2

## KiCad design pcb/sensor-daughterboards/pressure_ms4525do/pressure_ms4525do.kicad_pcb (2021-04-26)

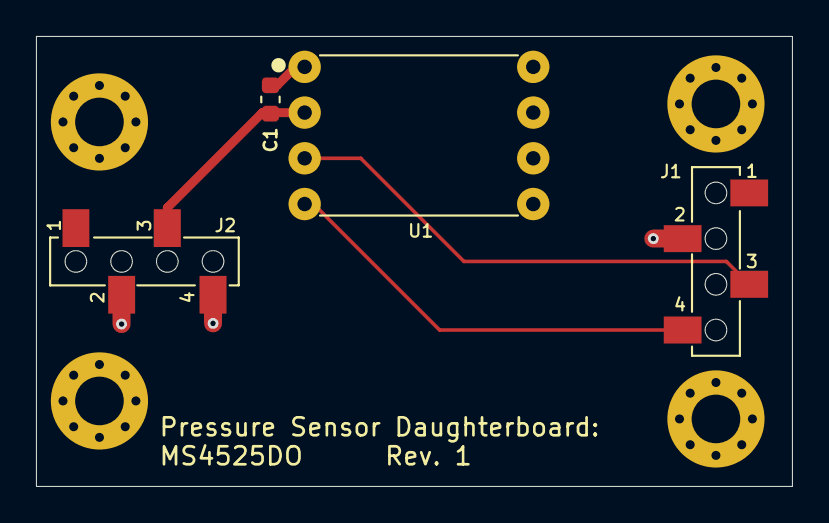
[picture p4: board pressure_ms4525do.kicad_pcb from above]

Board: 2 copper layers, 42.0 x 25.0 mm, 8 parts (0 on the bottom side), 4 nets.

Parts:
C1: 1uF; C_0603_1608Metric
H1, H2, H3, H4: M2.5; MountingHole_2.7mm_M2.5_Pad_Via
J1, J2: Main board connections (bottom entry); PinSocket_1x04_P2.54mm_Vertical_SMD_TE_1241152-4
U1: MS4525DO-DS5AI001DP; TE_MS4525DO-DSxxxxxxDP

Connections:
+3.3V_Sns: C1.2, J2.3, U1.2
/SCL: J1.4, U1.4
/SDA: J1.3, U1.3
GND: C1.1, J1.2, J2.2, J2.4, U1.1

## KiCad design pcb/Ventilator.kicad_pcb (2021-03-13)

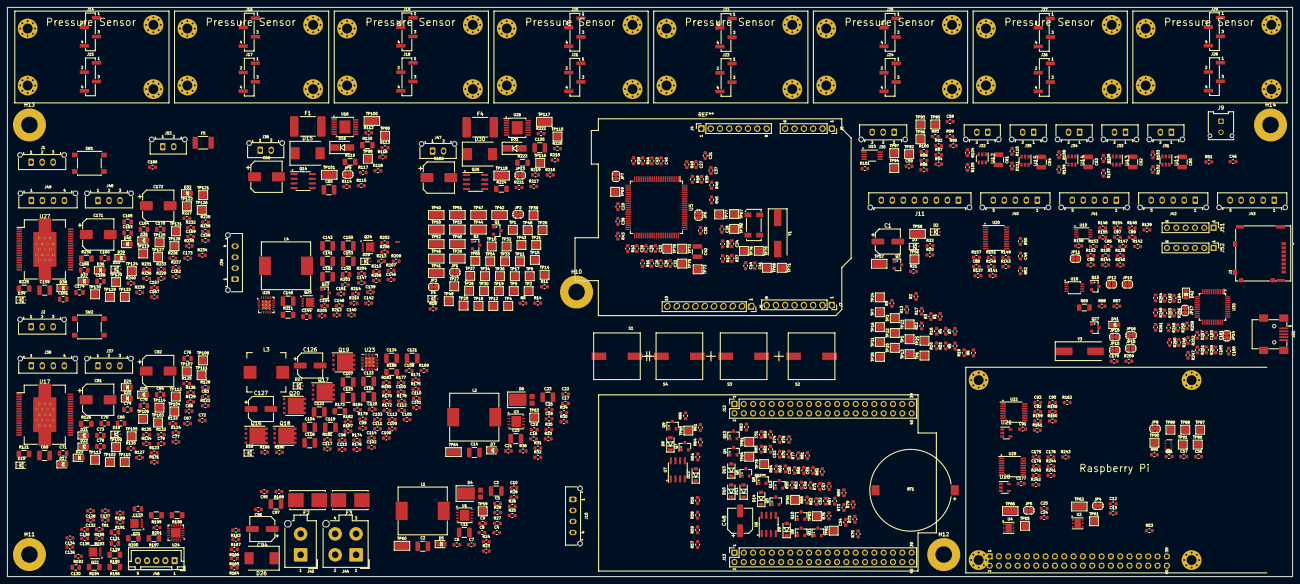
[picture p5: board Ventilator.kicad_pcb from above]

Board: 2 copper layers, 350.0 x 155.0 mm, 784 parts (1 on the bottom side), 430 nets, no tracks yet.

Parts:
BT1: CR2016; BatteryHolder_CR2016_MPD_BLP2016SM-G
C1, C48, C94, C126, C127: 33uF; CP_Elec_6.3x7.7
C2, C3, C14, C15, C42, C60, C61, C62, C63, C64, C65, C69, C97, C104, C107, C116, C118, C119, C121, C122, C123, C124, C125, C141, C143, C149, C150, C152, C153, C155, C159: 10uF; C_1210_3225Metric
C4, C8, C9, C16, C20, C21, C26, C32, C36, C37, C38, C39, C40, C41, C43, C45, C47, C50, C53, C56, C57, C58, C67, C68, C72, C77, C79, C85, C86, C87, C89, C90, C91, C92, C100, C101, C102, C111, C112, C113, C132, C138, C142, C146, C148, C157, C158, C162, C167, C169, C175, C176, C177, C181, C182, C183, C184, C185: 100nF; C_0603_1608Metric
C5, C17, C51, C52, C54, C55, C83, C95, C96, C103, C106, C117, C128, C134, C135, C136, C137, C173: 10nF; C_0603_1608Metric
C6, C18: 4.7nF; C_0603_1608Metric
C7, C19: 47pF; C_0603_1608Metric
C10, C12, C13, C22, C24, C25, C31, C35, C44, C46, C49, C59, C93, C105, C110, C151, C154, C178, C186: 1uF; C_0603_1608Metric
C11, C23: 47uF; C_1210_3225Metric
C27, C28: TBD; C_0603_1608Metric
C29, C30, C179, C180: 18pF; C_0603_1608Metric
C33, C34: 6.8pF; C_0603_1608Metric
C66, C81, C82, C156, C171, C172: 68uF; CP_Elec_8x10
C70, C71, C73, C74, C75, C76, C78, C80, C84, C144, C145, C160, C161, C163, C164, C165, C166, C168, C170, C174: 220nF; C_0805_2012Metric
C88: DNP; C_0603_1608Metric
C98: 1nF; C_0603_1608Metric
C99, C109: 47nF; C_0603_1608Metric
C108, C114, C115, C120, C140, C147: 100pF; C_0603_1608Metric
C129, C130, C131, C133: 470nF; C_0805_2012Metric
C139: 2.7nF; C_0603_1608Metric
D1, D2, D3, D18, D19, D27, D28, D29, D33, D34: BAT54J; D_SOD-323F
D4, D6: PDS760; D_PowerDI-5
D5, D7, D17, D32, D41: Green; LED_0805_2012Metric
D8: 2.0V; D_SOD-123
D9, D10: 3.3V; D_SOD-123
D11, D12, D13, D14: 1N4448W; D_SOD-123
D15, D26, D30: 20V; D_SMC
D16, D31: ES2B; D_SMA
D20, D21, D22, D23, D24, D25, D35, D36, D37, D38, D39, D40: Yellow; LED_0805_2012Metric
D42: Red; LED_0805_2012Metric
F1, F4: 2A; Fuse_2920_Bel_fuse
F2, F3: 10A; Fuseholder_Littelfuse_OMNI-BLOK-154
F5: 1.1A 16V; Fuse_1812_4532Metric_Castellated
H1: RaspberryPi
H2, H3, H4, H5, H6, H7, H8, H9: Pressure_sensor_daughterboard
H10, H11, H12, H13, H14: MountingHole_Pad; MountingHole_4.5mm_Pad
J1: Optical end stop 1; Molex_Micro-Fit_3.0_43650-0315_1x03_P3.00mm_Vertical
J2: Optical end stop 2; Molex_Micro-Fit_3.0_43650-0315_1x03_P3.00mm_Vertical
J3: 503182-1852; SD_Molex_5031821852
J4, J7: Arduino Connector; PinSocket_1x08_P2.54mm_Vertical
J5: Arduino Connector; PinSocket_1x06_P2.54mm_Vertical
J6: Arduino Connector; PinSocket_1x10_P2.54mm_Vertical
J8: Raspberry Pi; PinHeader_2x20_P2.54mm_Vertical
J9: Touchscreen power; Molex_Micro-Fit_3.0_43045-0212_2x01_P3.00mm_Vertical
J10: Alarm Battery (4x AA); Molex_Micro-Fit_3.0_43650-0415_1x04_P3.00mm_Vertical
J11: Cable to indicator board; Molex_Micro-Fit_3.0_43650-0815_1x08_P3.00mm_Vertical
J12: Mates J4 on BeMicro MAX10; PinSocket_2x20_P2.54mm_Vertical
J13: Mates J5 on BeMicro MAX10; PinSocket_2x20_P2.54mm_Vertical
J14, J15, J16, J17, J18, J19, J20, J21, J22, J23, J24, J25, J26, J27, J28, J29: Pressure sensor daughterboard; PinHeader_1x04_P2.54mm_Vertical_SMD_Pin1Right
J30: Oxygen sensor; Molex_Micro-Fit_3.0_43650-0315_1x03_P3.00mm_Vertical
J31, J32, J33, J34, J35: Temperature sensor (NTC); Molex_Micro-Fit_3.0_43650-0215_1x02_P3.00mm_Vertical
J36, J47: Solenoid; Molex_Micro-Fit_3.0_43650-0215_1x02_P3.00mm_Vertical
J37, J48: Limit switch; Molex_Micro-Fit_3.0_43650-0315_1x03_P3.00mm_Vertical
J38, J49: Stepper Motor Windings; Molex_Micro-Fit_3.0_43650-0415_1x04_P3.00mm_Vertical
J39: Molex Micro-Fit; Molex_Micro-Fit_3.0_43650-0415_1x04_P3.00mm_Vertical
J40, J41, J42, J43: Molex Micro-Fit; Molex_Micro-Fit_3.0_43650-0515_1x05_P3.00mm_Vertical
J44: POWER-ENTRY MegaFit 2x2; Molex_Mega-Fit_76829-0104_2x02_P5.70mm_Vertical
J45: BAT-PWR MegaFit 2x1; Molex_Mega-Fit_76829-0102_2x01_P5.70mm_Vertical
J46: BAT-BALANCE JST XH 5-pin; JST_XH_B5B-XH-A_1x05_P2.50mm_Vertical
J50: USB B micro; USB_Mini-B_Wuerth_65100516121_Horizontal
J51: Backup debug in for cycle controller; PinHeader_1x06_P2.54mm_Vertical
J52: Debug in for ST-LINK; PinHeader_1x06_P2.54mm_Vertical
J53: Fan; Molex_Micro-Fit_3.0_43650-0215_1x02_P3.00mm_Vertical
JP1, JP2, JP3, JP4, JP5, JP8, JP9, JP10, JP11, JP13, JP14, JP15, JP16, JP17, JP19: Jumper_NC_Small; SolderJumper-2_P1.3mm_Bridged_RoundedPad1.0x1.5mm
JP6: Jumper; SolderJumper-2_P1.3mm_Open_RoundedPad1.0x1.5mm
JP7: Jumper; SolderJumper-2_P1.3mm_Bridged_RoundedPad1.0x1.5mm
JP12, JP18: Jumper_NO_Small; SolderJumper-2_P1.3mm_Open_RoundedPad1.0x1.5mm
L1, L2: 15uH; L_TDK_SPM12565VT
L3: SRP1038A-3R3M; L_Bourns-SRP1038
L4: 6.8uH; L_TDK_SPM12565VT
NT1: Net-Tie_2; NetTie-2_SMD_Pad0.5mm
Q1, Q2, Q3, Q4, Q5, Q6, Q8, Q9, Q11, Q12, Q13, Q15, Q23, Q27: MMBT3904; SOT-23
Q7, Q10: MMBT2907A; SOT-23
Q14, Q26: FDS4672A; SOIC-8_3.9x4.9mm_P1.27mm
Q16, Q17, Q18, Q19: BSC065N06LS5ATMA1; VSONP-8-1EP_5x6_P1.27mm
Q20: SI7145DP-T1-GE3; VSONP-8-1EP_5x6_P1.27mm
Q21, Q22, Q24, Q25: BSZ019N03LSATMA1; VSON-8-SGD_3.3x3.3mm_P0.65mm_NexFET
R1, R2, R3, R4, R5, R6, R7, R8, R20, R21, R73, R74, R79, R80, R82, R83, R85, R86, R115, R125, R128, R131, R132, R133, R134, R135, R136, R139, R141, R189, R195, R219, R229, R232, R235, R236, R237, R238, R239, R240, R255, R256: 1k; R_0603_1608Metric
R9, R18, R19, R41, R87, R88, R142, R143, R144, R145, R146, R147, R148, R149, R150, R151, R152, R153, R253, R254: 4.7k; R_0603_1608Metric
R10, R11, R12, R13, R14, R15, R16, R17, R63, R66, R71, R72, R112, R170, R172, R176, R212, R216, R246, R257, R258: 100k; R_0603_1608Metric
R22, R39, R40, R42, R43, R45, R46, R47, R48, R49, R50, R51, R52, R53, R90, R91, R122, R123, R127, R140, R154, R155, R156, R157, R158, R177, R178, R184, R186, R226, R227, R231, R241, R248, R249: 0; R_0603_1608Metric
R23, R30, R171, R175: 316k; R_0603_1608Metric
R24, R27, R31, R34, R69, R114, R208, R218: 52.3k; R_0603_1608Metric
R25, R32, R70: 249k; R_0603_1608Metric
R26, R33: 16.9k; R_0603_1608Metric
R28, R35, R37, R44, R54, R55, R56, R57, R58, R59, R60, R61, R65, R68, R76, R81, R84, R92, R93, R94, R95, R96, R97, R98, R100, R113, R117, R137, R138, R160, R162, R181, R182, R185, R191, R202, R203, R204, R205, R207, R213, R215, R217, R221, R243, R245, R250, R261: 10k; R_0603_1608Metric
R29, R36, R64, R99, R118, R222: 2k; R_0603_1608Metric
R38, R192, R193, R252, R260: 100; R_0603_1608Metric
R62, R77, R78, R214: 1M; R_0603_1608Metric
R67, R163, R166, R169: 442k; R_0603_1608Metric
R75: 680; R_0603_1608Metric
R89, R119, R120, R121, R126, R223, R224, R225, R230: 0; R_1206_3216Metric
R101, R116, R220, R247: 1.5k; R_0603_1608Metric
R102, R104, R106, R108, R110: 220 0.1%; R_0603_1608Metric
R103, R105, R107, R109, R111: 10k 0.1%; R_0603_1608Metric
R124, R129, R130, R164, R165, R167, R168, R228, R233, R234, R251: 39k; R_0603_1608Metric
R159, R161, R242, R244, R259: DNP; R_0603_1608Metric
R173, R188, R194, R200: 0.01; R_1206_3216Metric
R174, R201, R209, R210: 10; R_0603_1608Metric
R179, R180: 4.02k; R_0603_1608Metric
R183: 3M; R_0603_1608Metric
R187: 30.1k; R_0603_1608Metric
R190: 2k; R_1206_3216Metric
R196, R197, R198, R199: 49.9; R_1206_3216Metric
R206: 6.49k; R_0603_1608Metric
R211: 0.006; R_1206_3216Metric
S1, S2, S3, S4: CT-1205H-SMT; CT-1205H-SMT-TR
SW1: User TBD; SW_Push_6x6
SW2: Reset CC; SW_Push_6x6
TH1: 10k; R_0603_1608Metric
TP1, TP2, TP3, TP4, TP5, TP6, TP10, TP11, TP12, TP13, TP14, TP15, TP16, TP17, TP23, TP24, TP25, TP26, TP27, TP28, TP29, TP30, TP31, TP32, TP33, TP34, TP56, TP80, TP81, TP82, TP83, TP84, TP85, TP97, TP98, TP99, TP115, TP116: TP; TestPoint_Pad_2.0x2.0mm
TP7: PG-12V; TestPoint_Pad_2.0x2.0mm
TP8: PMon-IBat; TestPoint_Pad_2.0x2.0mm
TP9: PMon-IAdp; TestPoint_Pad_2.0x2.0mm
TP18: Stepper-ADC-In1; TestPoint_Pad_2.0x2.0mm
TP19: Stepper-ADC-In2; TestPoint_Pad_2.0x2.0mm
TP20: UART-Rx-STM-Tx-STLink; TestPoint_Pad_2.0x2.0mm
TP21: UART-Tx-STM-Rx-STLink; TestPoint_Pad_2.0x2.0mm
TP22: FPGA-ADC-nInt; TestPoint_Pad_2.0x2.0mm
TP35: PSol-CS1; TestPoint_Pad_2.0x2.0mm
TP36: CC-SDA; TestPoint_Pad_2.0x2.0mm
TP37: Low-Alarm-Bat; TestPoint_Pad_2.0x2.0mm
TP38: CC-SCL; TestPoint_Pad_2.0x2.0mm
TP39, TP40, TP41, TP42, TP44, TP45, TP46, TP47, TP50, TP51, TP52, TP53, TP57, TP58, TP60, TP62, TP64, TP66, TP100, TP101, TP117, TP118: TestPoint_Flag; TestPoint_Keystone_5019_Minature
TP43: PSol-CS2; TestPoint_Pad_2.0x2.0mm
TP48: UART-RTS-STM-CTS-RPi; TestPoint_Pad_2.0x2.0mm
TP49: UART-CTS-STM-RTS-RPi; TestPoint_Pad_2.0x2.0mm
TP54: UART-Tx-RPi-Rx-STM; TestPoint_Pad_2.0x2.0mm
TP55: UART-Rx-RPi-Tx-STM; TestPoint_Pad_2.0x2.0mm
TP59, TP61, TP63, TP65: ~Power Good; TestPoint_Pad_2.0x2.0mm
TP67: SPI-MISO; TestPoint_Pad_2.0x2.0mm
TP68: SPI-MOSI; TestPoint_Pad_2.0x2.0mm
TP69: SPI-SCLK; TestPoint_Pad_2.0x2.0mm
TP70: uSD-nCS; TestPoint_Pad_2.0x2.0mm
TP71: PD3; TestPoint_Pad_2.0x2.0mm
TP72: PD4; TestPoint_Pad_2.0x2.0mm
TP73: PD5; TestPoint_Pad_2.0x2.0mm
TP74: PD6; TestPoint_Pad_2.0x2.0mm
TP75: PE0; TestPoint_Pad_2.0x2.0mm
TP76: PE1; TestPoint_Pad_2.0x2.0mm
TP77: PE2; TestPoint_Pad_2.0x2.0mm
TP78: PE3; TestPoint_Pad_2.0x2.0mm
TP79: PD-Alarm; TestPoint_Pad_2.0x2.0mm
TP86: Inh-Flow; TestPoint_Pad_2.0x2.0mm
TP87: Exh-Flow; TestPoint_Pad_2.0x2.0mm
TP88: Oxy-Flow; TestPoint_Pad_2.0x2.0mm
TP89: Oxy-Pressure; TestPoint_Pad_2.0x2.0mm
TP90: Mix-Tank-Pressure; TestPoint_Pad_2.0x2.0mm
TP91: Patient-Pressure; TestPoint_Pad_2.0x2.0mm
TP92: Stepper1-Temp; TestPoint_Pad_2.0x2.0mm
TP93: Stepper2-Temp; TestPoint_Pad_2.0x2.0mm
TP94: Blower-Temp; TestPoint_Pad_2.0x2.0mm
TP95: Batt-Temp; TestPoint_Pad_2.0x2.0mm
TP96: Spare-Temp; TestPoint_Pad_2.0x2.0mm
TP102, TP119: nCS; TestPoint_Pad_2.0x2.0mm
TP103, TP120: StCk; TestPoint_Pad_2.0x2.0mm
TP104, TP121: SDI; TestPoint_Pad_2.0x2.0mm
TP105, TP122: CK; TestPoint_Pad_2.0x2.0mm
TP106, TP123: OscIn; TestPoint_Pad_2.0x2.0mm
TP107, TP124: OscOut; TestPoint_Pad_2.0x2.0mm
TP108, TP125: SDO; TestPoint_Pad_2.0x2.0mm
TP109, TP126: nBusy-Sync; TestPoint_Pad_2.0x2.0mm
TP110, TP127: nFlag; TestPoint_Pad_2.0x2.0mm
TP111, TP128: Out-A1; TestPoint_Pad_2.0x2.0mm
TP112, TP129: Out-A2; TestPoint_Pad_2.0x2.0mm
TP113, TP130: Out-B1; TestPoint_Pad_2.0x2.0mm
TP114, TP131: Out-B2; TestPoint_Pad_2.0x2.0mm
U1, U3: TPS54561; WSON-10-1EP_4x4mm_P0.8mm_EP2.6x3mm
U2, U4: LD39050PU33R; DFN-6-1EP_3x3mm_P0.95mm_EP1.75x2.5mm
U5: STM32L496VGT; LQFP-100_14x14mm_P0.5mm
U6, U7: TLC555; SOIC-8_3.9x4.9mm_P1.27mm
U8: TL431LI; SOT-23
U9: BMP280; Bosch_BMP280
U10: INA333AIDGKR; VSSOP-8_3.0x3.0mm_P0.65mm
U11, U12, U13, U14, U15: USBLC6-2SC6; SOT-23-6
U16, U26: TPS1H100A; TSSOP-14-1EP_4.4x5mm_P0.65mm
U17, U27: L6470PD; ST_POWERSO36_ThermalVias
U18: 24LC256T-I_MS; TSSOP-8_3x3mm_P0.65mm
U19: SN74LVC2T45DCTR; SSOP-8_2.95x2.8mm_P0.65mm
U20: TCA9544APWR; TSSOP-20_4.4x6.5mm_P0.65mm
U21, U28: LM4120-IM5X-3.3; SOT-23-5
U22, U29: ADC128D818; TSSOP-16_4.4x5mm_P0.65mm
U23: BQ24773; QFN-28-1EP_4x4mm_P0.4mm_EP2.6x2.6mm_ThermalVias
U24: MAX17320G20+; WQFN-24-1EP_4x4mm_P0.5mm_EP2.6x2.6mm
U25: LM5141; VQFN-24-1EP_4x4mm_P0.5mm_EP2.45x2.45mm_ThermalVias
U30: STM32F103CBT6; LQFP-48_7x7mm_P0.5mm
Y1, Y3: 8 Mhz; Crystal_SMD_HC49-SD
Y2: 32.768 kHz; Crystal_SMD_Abracon_ABS25

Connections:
+3.3V_Ctrl: C13.2, C31.1, C32.1, C38.1, C39.1, C40.1, C41.1, C42.1, C69.1, C77.1, C79.2, C85.2, C86.2, C89.2, C92.2, C93.2, C159.1, C167.1, C169.2, C182.2, C183.2, C184.2, C185.2, D1.1, D8.1, J3.4, J4.2, J4.4, J51.1, J52.1, JP3.1, JP6.2, JP10.1, JP18.1, Q27.2, R5.2, R9.1, R18.1, R19.1, R37.1, R41.2, R113.1, R121.2, R124.2, R127.2, R128.1, R129.2, R130.2, R132.2, R133.2, R142.1, R143.1, R144.1, R145.1, R146.1, R147.1, R148.1, R149.1, R150.1, R151.1, R152.1, R153.1, R154.2, R155.2, R156.2, R157.2, R158.2, R159.2, R161.2, R181.2, R185.1, R215.1, R217.1, R225.2, R228.2, R231.2, R232.1, R233.2, R234.2, R236.2, R237.2, R253.2, R255.1, R258.1, TP62.1, U2.4, U5.11, U5.28, U5.50, U5.73, U5.75, U5.100, U16.12, U17.9, U17.24, U18.8, U19.1, U19.5, U20.20, U22.5, U26.12, U27.9, U27.24, U30.1, U30.9, U30.24, U30.36, U30.48
+3.3V_FPGA: C177.2, C178.2, J12.1, J12.2, J13.29, R87.1, R88.1, R241.2, R242.2, R244.2, U29.5
+3.3V_Sns: C25.2, C43.1, C44.1, C56.2, C57.2, C58.2, J14.3, J16.3, J18.3, J20.3, J22.3, J24.3, J26.3, J28.3, R45.2, R93.2, R95.2, R102.2, R104.2, R106.2, R108.2, R110.2, TP66.1, U4.4, U5.22, U9.2, U9.6, U9.8, U10.7, U11.5, U12.5, U13.5, U14.5, U15.5
+3V3_Rpi: J8.1, J8.17, R50.1, R52.1
+5V: C21.2, C22.2, C23.2, C24.2, C90.2, C175.2, D2.2, D9.1, D10.1, D11.2, J1.1, J4.5, J4.8, J11.2, JP5.2, JP11.1, L2.2, R22.1, R34.1, R36.1, R89.2, S2.1, S3.1, TP64.1, U4.6, U21.3, U21.4, U28.3, U28.4
+5V_GUI: C9.2, C10.2, C11.2, C45.1, C46.1, J8.2, J8.4, J9.2, L1.2, R27.1, R29.1, S4.1, TP60.1
+5V_Sns: C1.1, J14.1, J16.1, J18.1, J20.1, J22.1, J24.1, J26.1, J28.1, R22.2, TP58.1
+5V_USB: D3.2, J50.1, R250.2
+12V: C147.2, C149.1, C150.1, C152.1, C153.1, C186.1, F5.2, R126.2, R211.1, R212.1, R214.1, R230.2, U25.17
+12V_Step1: C70.1, C71.1, C73.1, C74.1, C75.1, C76.1, C78.1, C80.1, C81.1, C82.1, C84.1, C160.1, C161.1, C163.1, C164.1, C165.1, C166.1, C168.1, C170.1, C171.1, C172.1, C174.1, D18.2, D33.2, R122.2, R126.1, R226.2, R230.1, U17.4, U17.5, U17.15, U17.16, U17.22, U17.23, U17.33, U17.34, U27.4, U27.5, U27.15, U27.16, U27.22, U27.23, U27.33, U27.34
+BATT: C48.1, C50.2, C53.2, D11.1, Q7.2, Q10.3, R56.2, R61.2, R66.2, R69.2, R75.2, S1.1, U6.8, U7.8
+VLink: C2.1, C3.1, C4.2, C14.1, C15.1, C16.2, C65.1, C66.1, C141.1, C143.1, C155.1, C156.1, J44.3, Q24.3, R23.1, R30.1, R120.1, R207.1, R224.1, U1.2, U3.2, U16.8, U16.9, U16.10, U25.15, U26.8, U26.9, U26.10
/Add'l aux functions/Blower-Enable: JP3.2, R139.2
/Alarms and Power Monitoring/Alarm-Bat: D14.2, J10.1, R71.1
/Alarms and Power Monitoring/Low-Alarm-Bat: Q10.2, R78.1, R81.1, R84.1, TP37.1, TP84.1
/Alarms and Power Monitoring/PD-Alarm: C47.2, D12.1, D13.1, R63.2, TP79.1, U6.4
/Aux-I2C-Switch-nINT: JP2.2, U20.17
/Bat-Alert: R3.1, U5.77, U24.7
/Blower-Ctrl: R137.1, U5.63, U19.2
/CC-Buzzer: J7.6, R79.1, TP82.1, U5.53
/CC-LED-G: J5.3, J11.3, U5.67
/CC-LED-R: J11.4, U5.65
/CC-LED-Y: J11.5, U5.66
/CC-SCL: J6.10, J15.4, J17.4, J19.4, J21.4, J23.4, J25.4, J27.4, J29.4, R19.2, R91.1, TP38.1, U5.95, U18.6, U20.18, U22.3, U23.12, U24.8
/CC-SDA: J6.9, J15.3, J17.3, J19.3, J21.3, J23.3, J25.3, J27.3, J29.3, R18.2, R90.1, TP36.1, U5.96, U18.5, U20.19, U22.2, U23.11, U24.9
/CC-Stepper-Reset: J7.3, R4.1, U5.48
/Cycle Controller/BOOT0: R44.2, U5.94
/Cycle Controller/PH0: JP1.1, JP2.1, R9.2, R42.1, U5.12
/Cycle Controller/RTC-Batt: BT1.1, C35.1, JP6.1, U5.6
/Cycle Controller/Stepper-Lim-Sw1: C27.2, R39.1, U5.78
/Cycle Controller/Stepper-Lim-Sw2: C28.2, R40.1, U5.79
/Cycle Controller/uSD-Detect: J3.Detect, R37.2, U5.64
/Cycle Controller/uSD-nCS: J3.2, TP70.1, U5.29
/Exh-Flow: J17.1, R10.2, TP87.1, U5.33
/FPGA's ADC/ADC0: R10.1, U29.16
/FPGA's ADC/ADC1: R11.1, U29.15
/FPGA's ADC/ADC2: R12.1, U29.14
/FPGA's ADC/ADC3: R13.1, U29.13
/FPGA's ADC/ADC4: R14.1, U29.12
/FPGA's ADC/ADC5: R15.1, U29.11
/FPGA's ADC/ADC6: R16.1, U29.10
/FPGA's ADC/ADC7: R17.1, U29.9
/FPGA's ADC/nINT: TP22.1, U29.6
/FPGA-Buzzer: J13.1, R82.1, TP83.1
/FPGA-Stepper-Reset: J13.7, R6.2
/GUI-Buzzer: J8.32, R85.1, TP85.1
/Inh-Flow: J5.2, J15.1, R12.2, TP86.1, U5.24
/Logic/Control Power Supplies/3.3V Logic Supply/In: C12.2, D2.1, D3.1, JP4.2, TP57.1, U2.6
/Logic/Control Power Supplies/5V Control Supply/Fb: R34.2, R35.1, U3.6
/Logic/Control Power Supplies/5V Control Supply/nEnable: R30.2, R31.1, U3.3
/Logic/Control Power Supplies/5V UI Supply/Fb: R27.2, R28.1, U1.6
/Logic/Control Power Supplies/5V UI Supply/nEnable: Q3.2, R23.2, R24.1, U1.3
/Low-Alarm-Bat: D1.2, R2.1, R84.2
/Mix-Tank-Pressure: J21.1, TP90.1, U5.17
/Oxygen-FiO2: C59.2, J5.6, R13.2, R101.2, TP97.1, U5.15
/Oxygen-Flow: J19.1, R11.2, TP88.1, U5.34
/Oxygen-Pressure: J25.1, R16.2, TP89.1, U5.18
/PMon-ACOK: J5.4, R185.2, U5.92, U23.5
/PMon-PSys: C114.1, R187.1, U22.11, U23.9
/PSol1-Ctrl: J6.1, R219.2, TP115.1, U5.47, U26.3
/PSol1-nFault: JP13.1, R217.2, U5.93
/PSol2-Ctrl: R115.2, TP98.1, U5.23, U16.3
/PSol2-nFault: JP9.1, R43.1, R113.2, U5.13
/PSol Driver, Spare/CS: R112.1, R114.1, TP43.1
/PSol Driver/CS: R216.1, R218.1, TP35.1
/Patient-Pressure: J5.5, J23.1, R14.2, TP91.1, U5.16
/Power Entry / Battery Handling/12V System Buck Converter/LM5141-AGND: C140.2, C142.1, C144.1, C145.1, C148.2, NT1.1, R204.2, R206.2, R208.2, U25.3, U25.6
/Power Entry / Battery Handling/12V System Buck Converter/LM5141-VCC: C151.2, C154.2, D29.2, U25.10
/Power Entry / Battery Handling/12V System Buck Converter/LM5141-VDDA: C148.1, R203.1, U25.2
/Power Entry / Battery Handling/Bat-N: C97.2, C128.2, C129.2, C130.2, C131.2, C135.2, C138.2, J45.1, R191.2, R194.1, R195.2, R200.1, TH1.2, U24.15, U24.20, U24.25
/Power Entry / Battery Handling/Bat-P: C97.1, C132.1, F3.2, Q22.1, R201.1
/Power Entry / Battery Handling/Battery Charger / Source Switching/Pack-P: D27.2, Q20.3, Q21.1, R166.1, R175.1, R189.1, R190.2, U23.17
/Power Entry / Battery Handling/Battery Charger / Source Switching/RegN: C110.1, R171.1, R182.2, U23.24
/Power Entry / Battery Handling/Battery Charger / Source Switching/VIn-Adp: C98.1, Q16.3, R169.1
/Power Entry / Battery Handling/PG-12V: R215.2, TP7.1, U25.21
/Power Entry / Battery Handling/PMon-IAdp: C120.1, TP9.1, U23.7
/Power Entry / Battery Handling/PMon-IBat: C115.1, TP8.1, U23.8
/Power Entry / Battery Handling/Power-Sw-P: C111.1, C113.1, C116.1, C117.1, C118.1, C119.1, C121.1, C122.1, C123.1, C124.1, C125.1, C126.1, C127.1, J44.4, L3.2, R188.2, U23.20
/Power Entry / Battery Handling/Vin-Adp: C94.1, D26.1, F2.1, R163.1
/STM Programmer for cycle controller/CC-SWCLK: J51.2, JP14.1, U5.76
/STM Programmer for cycle controller/CC-SWCLK-Out: JP14.2, U30.15, U30.26
/STM Programmer for cycle controller/CC-SWDIO: J51.4, JP15.1, U5.72
/STM Programmer for cycle controller/CC-SWDIO-Out: JP15.2, R260.2, U30.27
/STM Programmer for cycle controller/CC-SWO: J51.6, JP17.1, U5.89
/STM Programmer for cycle controller/CC-SWO-Out: JP17.2, U30.31
/STM Programmer for cycle controller/CC-nRST: C37.1, J4.3, J51.5, JP16.1, SW2.1, U5.14
/STM Programmer for cycle controller/CC-nRST-Out: JP16.2, U30.18
/STM Programmer for cycle controller/Prog-SWCLK: J52.2, U30.37
/STM Programmer for cycle controller/Prog-SWDIO: J52.4, U30.34
/STM Programmer for cycle controller/Prog-nRST: C181.2, J52.5, R258.2, U30.7
/STM Programmer for cycle controller/USB-D+: R248.1, U30.33
/STM Programmer for cycle controller/USB-D-: R249.2, U30.32
/STM Programmer for cycle controller/VSense: R253.1, R254.2, U30.10
/STM Programmer for cycle controller/nRenum-USB: R252.1, U30.38
/Safety FPGA/DIFF-RX-7+: J13.23, TP31.1
/Safety FPGA/DIFF-RX-7-: J13.24, TP32.1
/Safety FPGA/DIFF-RX-8+: J13.21, TP29.1
/Safety FPGA/DIFF-RX-8-: J13.22, TP30.1
/Safety FPGA/DIFF-RX-9+: J13.19, TP27.1
/Safety FPGA/DIFF-RX-9-: J13.20, TP28.1
/Safety FPGA/DIFF-RX-A+: J13.17, TP25.1
/Safety FPGA/DIFF-RX-A-: J13.18, TP26.1
/Safety FPGA/DIFF-RX-B+: J13.15, TP23.1
/Safety FPGA/DIFF-RX-B-: J13.16, TP24.1
/Safety FPGA/GPIO-11: J13.13, TP33.1
/Safety FPGA/GPIO-12: J13.14, TP34.1
/Safety FPGA/I2C-SCL-FPGA: J12.4, R88.2, U29.3
/Safety FPGA/I2C-SDA-FPGA: J12.3, R87.2, U29.2
/Stepper1-StCk: R124.1, TP103.1, U5.35, U17.32
/Stepper1-nBusy: D22.1, J6.3, R129.1, TP109.1, U5.51, U17.29
/Stepper2-StCk: J7.8, R228.1, TP120.1, U5.36, U27.32
/Stepper2-nBusy: D37.1, J6.2, R233.1, TP126.1, U5.52, U27.29
/Stepper Motor Driver (..)/ADC-In: C157.2, R226.1, R227.2, TP19.1, U27.8
/Stepper Motor Driver (..)/Out-A1: D40.2, J49.1, TP128.1, U27.2, U27.3
/Stepper Motor Driver (..)/Out-A2: D39.2, J49.2, TP129.1, U27.35, U27.36
/Stepper Motor Driver (..)/Out-B1: D38.2, J49.3, TP130.1, U27.17, U27.18
/Stepper Motor Driver (..)/Out-B2: D36.2, J49.4, TP131.1, U27.20, U27.21
/Stepper Motor Driver (..)/SDI: TP108.1, TP121.1, U17.25, U27.27
/Stepper Motor Driver (..)/Switch: R229.1, R231.1, U27.7
/Stepper Motor Driver (...)/ADC-In: C67.2, R122.1, R123.2, TP18.1, U17.8
/Stepper Motor Driver (...)/Out-A1: D25.2, J38.1, TP111.1, U17.2, U17.3
/Stepper Motor Driver (...)/Out-A2: D24.2, J38.2, TP112.1, U17.35, U17.36
/Stepper Motor Driver (...)/Out-B1: D23.2, J38.3, TP113.1, U17.17, U17.18
/Stepper Motor Driver (...)/Out-B2: D21.2, J38.4, TP114.1, U17.20, U17.21
/Stepper Motor Driver (...)/Switch: R125.1, R127.1, U17.7
/Stepper-MISO: J3.7, TP67.1, TP125.1, U5.31, U27.25
/Stepper-MOSI: J3.3, TP68.1, TP104.1, U5.32, U17.27
/Stepper-SCK: J3.5, TP69.1, TP105.1, TP122.1, U5.30, U17.26, U27.26
/Stepper-nCS: J7.5, TP102.1, TP119.1, U5.54, U17.30, U27.30
/Stepper-nFlag: D20.1, D35.1, J7.4, R130.1, R234.1, TP110.1, TP127.1, U5.37, U17.31, U27.31
/Stepper-nReset: C72.2, C162.2, Q1.2, Q2.2, R5.1, U17.6, U27.6
/SysMonADC-nINT: JP1.2, U22.6
/System Monitor ADC/ADC0: C60.1, R103.2, TP92.1, U11.4, U22.16
/System Monitor ADC/ADC1: C61.1, R105.2, TP93.1, U12.4, U22.15
/System Monitor ADC/ADC2: C62.1, R107.2, TP94.1, U13.4, U22.14
/System Monitor ADC/ADC3: C63.1, R109.2, TP95.1, U14.4, U22.13
/System Monitor ADC/ADC4: C64.1, R111.2, TP96.1, U15.4, U22.12
/UART-CTS-RPi-RTS-STM: J8.36, U5.71
/UART-CTS-STM-RTS-FPGA: J13.9, U5.91
/UART-RTS-RPi-CTS-STM: R1.1, U5.70
/UART-RTS-STM-CTS-FPGA: J13.8, U5.90
/UART-Rx-FPGA-Tx-RPi: J8.24, J13.5
/UART-Rx-RPi-Tx-STM: J7.2, J8.10, TP55.1, U5.68
/UART-Rx-STM-Tx-FPGA: J13.3, U5.83
/UART-Rx-STM-Tx-STLink: TP20.1, U5.26, U30.12
/UART-Tx-FPGA-Rx-RPi: J13.6, R7.2
/UART-Tx-RPi-Rx-STM: J7.1, R8.2, TP54.1, U5.69
/UART-Tx-STM-Rx-FPGA: J13.4, U5.80
/UART-Tx-STM-Rx-STLink: J7.7, TP21.1, U5.25, U30.13
/UI Computer/GPIO0(ID_SD): J8.27, TP10.1
/UI Computer/GPIO1(ID_SC): J8.28, TP11.1
/UI Computer/GPIO2(SDA): J8.3, TP12.1
/UI Computer/GPIO3(SCL): J8.5, TP13.1
/UI Computer/GPIO7(CE1): J8.26, TP14.1
/UI Computer/GPIO9(MISO): J8.21, R7.1
/UI Computer/GPIO10(MOSI): J8.19, TP15.1
/UI Computer/GPIO11(SCLK): J8.23, TP16.1
/UI Computer/GPIO13(PWM1): J8.33, TP17.1
/UI Computer/GPIO14(TXD): J8.8, R8.1
/UI Computer/GPIO17: J8.11, R1.2
/UI Computer/GPIO18(PCM_CLK): J8.12, R2.2
/UI Computer/GPIO19(PCM_FS): J8.35, R3.2
/UI Computer/GPIO20(PCM_DIN): J8.38, TP1.1
/UI Computer/GPIO21(PCM_DOUT): J8.40, TP2.1
/UI Computer/GPIO22: J8.15, TP3.1
/UI Computer/GPIO23: J8.16, TP4.1
/UI Computer/GPIO24: J8.18, TP5.1
/UI Computer/GPIO27: J8.13, TP6.1
/UI Computer/UI_ID0: J8.22, R52.2, R53.1
/UI Computer/UI_ID1: J8.37, R50.2, R51.1
/UI-LED-G: J8.7, J11.6
/UI-LED-R: J8.29, J11.7
/UI-LED-Y: J8.31, J11.8
/UI-Power-Off: J13.2, R20.1, R21.1, TP56.1
/VBat-Sense: C96.1, R166.2, R167.1, U22.10
/VSys-Power-Off: J13.10, R202.2
/Vin-Sense: C95.1, R17.2, R163.2, R164.1, U22.9
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

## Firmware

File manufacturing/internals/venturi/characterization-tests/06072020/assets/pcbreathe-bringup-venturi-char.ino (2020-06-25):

/*
# pcbreathe-bringup
# bringup test code for RespiraWorks Ventilator Mainboard Rev 1.0
use STM32duino and select appropriate board and COM port and use SWD programming

this branch of pcbreathe-bringup, pcbreathe-PinchValveCharacterization, was created to characterize the proportional stepper valves designed by Marc Auger and the venturi flow sensors designed by Ethan Chaleff for RespiraWorks.

This code was writted by Edwin Chiu for RespiraWorks.

## WHAT IT DOES:
* It sets the blower to a fixed power level and ramps through a series of position in the inhale limb pinch valve.
* For characterizing the pinch valves, it can be used with a low-dP flow sensors such as the AD Pneumotachograph downstream of the valve.  Note that you may want to remove the venturi for this test.
* It can also be used to provide varying flow rates for venturi sensor characterization.  In this case, put the venturi downstream of the valve and a reference flow sensor downstream of that.
* It supports an AMS5915_0100_D i2c differential pressure sensor on port I2C SENSOR D on the PCB.  Refer to the ICD if you need a pinout. (But the setup may have an adapter cable provided to plug directly into I2C SENSOR D.)

## SETTINGS:
* In the #defines below, most of the settings for this test can be edited
* STATE_PERIOD is the dwell time at each valve position setting
* CONTROL_PERIOD is the sampling rate of the data output
* The test will cycle from OPENPOS with increment STEPSIZE until it reaches CLOSEDSIZE.
* Then it will make a one-STATE_PERIOD blip to position BLIPPOS, this creates a clear signal to assists in aligninging the data with a reference data acquision setup.
* The test will then cycle back from CLOSEDPOS with increment STEPSIZE until it reaches OPENPOS.

## GETTING DATA OUT:
Outputs can be plotted and exported with Cypress PSoC Programmer (Bridge Control Panel Tool)
* Download and install, connect serial
* Tools > Protocol Configuration > serial 115200:8n1 > hit OK
* In the editor tab, use this command:

    ```RX8 [h=43] @1Key1 @0Key1 @1Key2 @0Key2 @1Key3 @0Key3 @1Key4 @0Key4 @1Key5 @0Key5 @1Key6 @0Key6 @1Key7 @0Key7```
* In order, each of these outputs is: Time(ms), Valve Position, Pressure dP, Inhale dP, Exhale dP, AMS5915 pressure, AMS5915 temperature
* The MPXV5004DPs come out as 14bit values and the scaling is ```kPa = 5*Value/16383-1```.  The AMS5915 is 14bit and the scaling is kPa = ```10*(Value-1638)/(14745-1638)```.
* The MPXV5004DP sensors are assigned to Pressure, Inhale, and Exhale on this board, but of course you can connect them to anything you want to measure
* The hypodermic needles can be useful for picking off pressures anywhere you have rubber tubing.
* Be careful not to poke yourself.
* Watch out for dynamic pressure effects when using the needles.  I have found better results by inserting the needle at an acute angle to the flow, pointing downstream, and retracting the needle such that the opening is near the sidewall of the hose.

![hypodermic needle pickoff](needle_pressure_pickoff.jpg)
* Chart > Variable Settings
* Tick Key1 through Key7, configure as int, and choose colors > hit OK
* Press >|< icon to connect to com port if necessary
* Click REPEAT button, go to Chart tab
* both traces should now be plotting
* Click STOP button to stop recording.
* Chart > Export Collected Data in the format of your choice.  Note that this method captures a maximum of 10,000 samples.  It will clip the beginning of your experiment if it is longer than 10k samples.
* You can run longer experiments within the 10k sample limit by increasing CONTROL_PERIOD, which will reduce the sampling rate.
* If you need more than 10k samples use a different logger (or use the TO FILE button instead of REPEAT, it will output hex data that you can copy-and-paste, so be prepared to do some post-processing)

## HOW TO USE THIS TEST (generic to pcbreathe-bringup):
* Follow the instructions on the https://github.com/inceptionev/pcbreathe-bringup readme to set up the hardware and the IDE.


## STM32duino setup
* To use this code, you will need to setup the Arduino IDE to talk to STM32.  Use this link for instructions: [http://www.emcu.eu/2017/03/13/how-to-use-stm32-and-arduino-ide/](http://www.emcu.eu/2017/03/13/how-to-use-stm32-and-arduino-ide/)
* To program this board, you will need to go to Tools... and select the following
    * Board: Nucleo-64
    * Board part number: L452RE
    * Upload method: Mass Storage
    * Port: [select the com port where you computer assigned the Nucleo]
    * other settings can be left on their defaults.
* Further dependencies.  You will also need to install the following packages to run this code (install by going to Tools...Manage Libraries... in your Arduino IDE and seaching for the below):
  * Adafruit SDD1306
  * Adafruit GFX
  * [powerSTEP01 arduino library](https://github.com/Megunolink/powerSTEP01_Arduino_Library) (may require manual install: follow the directions in the readme of the library.)
  * some folks have reported issues with the Mass Storage programming method (not enough space error).  Here are a couple things to try:
  * make sure you have the latest version of the Arduino IDE and the STM32duino board package (first link in this section up abobe).
  * If that doesn't work the "STM32CubeProgrammer (SWD)" programming option will almost certainly work.  However, to use the SWD mode you will need to download and install the [STM32CubeProgrammer](https://www.st.com/content/st_com/en/products/development-tools/software-development-tools/stm32-software-development-tools/stm32-programmers/stm32cubeprog.html#overview)
*/

#include <SPI.h>
#include <SD.h>
#include <powerSTEP01ArduinoLibrary.h>
#include <Wire.h>
#include <AMS5915.h>


//hardware definitions
//PCB pins
#define PIN_PRES PA1
#define PIN_INH PA4
#define PIN_EXH PB0
#define PIN_VSENSE PA0
#define PIN_BUZZER PB4
#define PIN_BLOWER PB3
#define PIN_SOLENOID PA11
#define PIN_HEATER PA8
#define PIN_LED_R PC13
#define PIN_LED_Y PC14
#define PIN_LED_G PC15
const int chipSelect = PA15;  //SD card chip select
// Pin definitions for the X-NUCLEO-IHM03A1 (stepper driver)
#define nCS_PIN PB6
#define STCK_PIN PC7
#define nSTBY_nRESET_PIN PA9
#define nBUSY_PIN PB5

//Pinch valve motion settings
#define STARTSTROKE 7000
#define OPENPOS 2250
#define CLOSEDPOS 6250
#define BLIPPOS 4500

//i2c test device definitions

//instantiate stepper driver
powerSTEP driverINH(0, nCS_PIN, nSTBY_nRESET_PIN);
powerSTEP driverEXH(1, nCS_PIN, nSTBY_nRESET_PIN);

//instantiate i2c sensor
AMS5915 sPress(Wire,0x28,AMS5915::AMS5915_0100_D);

//test parameters
#define BUZZER_VOL 0 //buzzer volume
#define STATE_PERIOD 2000 //actuation cycle timing in ms
#define CONTROL_PERIOD 50 // control cycle period
#define STEPSIZE 200 //for pinchvalve characterization, amount to step the valve each time (6500-4000)/20 = 125

#define BLOWER_HIGH 255 //blower high throttle command
#define BLOWER_LOW 255 //blower low throttle command

//create state machine variables
int pressure = 0;
int flow_inh = 0;
int flow_exh = 0;
int vsense = 0;
int inh_flow =0;
int exh_flow = 0;
int state = 0;
unsigned int now = 0;
int cyclecounter=0;
int statecounter=0;
int commandINH=OPENPOS;
uint16_t ams_dP = 0;
uint16_t ams_temp = 0;

//create objects for SD card test

//instantiate USART3

void setup() {
  // put your setup code here, to run once:

  // Open serial communications and wait for port to open:
  Serial.begin(115200);

  //set hw pin modes
  pinMode(PIN_LED_R,OUTPUT);
  pinMode(PIN_LED_Y,OUTPUT);
  pinMode(PIN_LED_G,OUTPUT);
  pinMode(PIN_BUZZER,OUTPUT);
  pinMode(PIN_BLOWER,OUTPUT);
  pinMode(PIN_SOLENOID,OUTPUT);
  pinMode(PIN_HEATER,OUTPUT);
  //Stepper driver pins
  pinMode(nSTBY_nRESET_PIN, OUTPUT);
  pinMode(nCS_PIN, OUTPUT);
  pinMode(MOSI, OUTPUT);
  pinMode(MISO, OUTPUT);
  pinMode(SCK, OUTPUT);

  analogReadResolution(14);

  // Reset powerSTEP and set CS
  digitalWrite(nSTBY_nRESET_PIN, HIGH);
  digitalWrite(nSTBY_nRESET_PIN, LOW);
  digitalWrite(nSTBY_nRESET_PIN, HIGH);
  digitalWrite(nCS_PIN, HIGH);

  // Start SPI
  SPI.begin();
  SPI.setDataMode(SPI_MODE3);

  // Configure powerSTEP
  driverEXH.SPIPortConnect(&SPI); // give library the SPI port
  driverINH.SPIPortConnect(&SPI); // give library the SPI port

  driverEXH.configSyncPin(BUSY_PIN, 0);
  driverINH.configSyncPin(BUSY_PIN, 0); // use SYNC/nBUSY pin as nBUSY,
                                     // thus syncSteps (2nd paramater) does nothing

  driverEXH.configStepMode(STEP_FS_128);
  driverINH.configStepMode(STEP_FS_128); // 1/128 microstepping, full steps = STEP_FS,
                                // options: 1, 1/2, 1/4, 1/8, 1/16, 1/32, 1/64, 1/128

  driverEXH.setMaxSpeed(1000);
  driverINH.setMaxSpeed(1000); // max speed in units of full steps/s
  driverEXH.setFullSpeed(2000);
  driverINH.setFullSpeed(2000); // full steps/s threshold for disabling microstepping
  driverEXH.setAcc(2000);
  driverINH.setAcc(2000); // full steps/s^2 acceleration
  driverEXH.setDec(2000);
  driverINH.setDec(2000); // full steps/s^2 deceleration

  driverEXH.setSlewRate(SR_520V_us);
  driverINH.setSlewRate(SR_520V_us); // faster may give more torque (but also EM noise),
                                  // options are: 114, 220, 400, 520, 790, 980(V/us)

  driverEXH.setOCThreshold(8);
  driverINH.setOCThreshold(8); // over-current threshold for the 2.8A NEMA23 motor
                            // used in testing. If your motor stops working for
                            // no apparent reason, it's probably this. Start low
                            // and increase until it doesn't trip, then maybe
                            // add one to avoid misfires. Can prevent catastrophic
                            // failures caused by shorts

  driverEXH.setOCShutdown(OC_SD_ENABLE);
  driverINH.setOCShutdown(OC_SD_ENABLE); // shutdown motor bridge on over-current event
                                      // to protect against permanant damage

  driverEXH.setPWMFreq(PWM_DIV_1, PWM_MUL_0_75);
  driverINH.setPWMFreq(PWM_DIV_1, PWM_MUL_0_75); // 16MHz*0.75/(512*1) = 23.4375kHz
                            // power is supplied to stepper phases as a sin wave,
                            // frequency is set by two PWM modulators,
                            // Fpwm = Fosc*m/(512*N), N and m are set by DIV and MUL,
                            // options: DIV: 1, 2, 3, 4, 5, 6, 7,
                            // MUL: 0.625, 0.75, 0.875, 1, 1.25, 1.5, 1.75, 2

  driverEXH.setVoltageComp(VS_COMP_DISABLE);
  driverINH.setVoltageComp(VS_COMP_DISABLE); // no compensation for variation in Vs as
                                          // ADC voltage divider is not populated
  driverEXH.setSwitchMode(SW_USER);
  driverINH.setSwitchMode(SW_USER); // switch doesn't trigger stop, status can be read.
                                 // SW_HARD_STOP: TP1 causes hard stop on connection
                                 // to GND, you get stuck on switch after homing

  driverEXH.setOscMode(INT_16MHZ);
  driverINH.setOscMode(INT_16MHZ); // 16MHz internal oscillator as clock source

  // KVAL registers set the power to the motor by adjusting the PWM duty cycle,
  // use a value between 0-255 where 0 = no power, 255 = full power.
  // Start low and monitor the motor temperature until you find a safe balance
  // between power and temperature. Only use what you need
  driverEXH.setRunKVAL(60);
  driverINH.setRunKVAL(60); //2.8V in voltage mode for 2A max on 1.4ohm coils
  driverEXH.setAccKVAL(60);
  driverINH.setAccKVAL(60);
  driverEXH.setDecKVAL(60);
  driverINH.setDecKVAL(60);
  driverEXH.setHoldKVAL(32);
  driverINH.setHoldKVAL(32);
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

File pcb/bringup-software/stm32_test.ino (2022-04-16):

// Hardware tests: exercises buzzer, system monitor ADC, power outputs, etc.
// for electronics testing NOTE: this is terrible-quality code with zero error
// checking - do not re-use any of it anywhere

// Library doesn't have ...L496VG, so we use the ...L496ZG instead:
// the P**<->peripheral mapping is the same either way, even though
// the pin numbers are different

// Install in board manager: STM32 MCU based boards
// Install in library manager: Ponoor L6470 Library
// Board: "Generic STM32L4 series"
// Board part number: "Generic L496ZGTx"
// U(S)ART support: "Enabled (generic 'Serial')"
// Upload method: "STM32CubeProgrammer (SWD)"

// GPIO
#define LED_PIN PA8
#define BZR_PIN PB14

// PWM outputs
#define PSOL_TIM TIM2
#define PSOL1_PIN PB10 // tim2_ch3
#define PSOL1_TIM_CH 3
#define PSOL2_PIN PA0 // tim2_ch1, tim5_ch1
#define PSOL2_TIM_CH 1
#define BLOWER_CTRL_TIM TIM3
#define BLOWER_CTRL_PIN PC6 // tim3_ch1, tim8_ch1
#define BLOWER_CTRL_TIM_CH 1

// stepper drivers / SPI
#define CS_PIN PB15
#define MOSI_PIN PA7
#define MISO_PIN PA6
#define SCLK_PIN PA5
#define STEP_RST_PIN PB11
#define STEP1_BUSY_PIN PB12
#define STEP2_BUSY_PIN PB13

// I2C
#define SDA_PIN PB9
#define SCL_PIN PB8
// external ADC (ADC128D818)
#define EXT_ADC_ADDR 0x1D // both A0 and A1 tied low
// power manager/battery charger (bq24773)
#define PWR_MAN_ADDR                                                           \
  0x6A // I2C-mode address; listed as 0xD4 left-aligned (with assumed R/W bit =
       // 0) but library takes addresses right-aligned
#define PWR_MAN_CHG_OPT_0_REG 0x00
#define PWR_MAN_CHG_OPT_1_REG 0x02
#define PWR_MAN_CHG_OPT_2_REG 0x10
#define PWR_MAN_PROCHOT_OPT_0_REG 0x04
#define PWR_MAN_PROCHOT_OPT_1_REG 0x06
#define PWR_MAN_CHG_CURR_REG 0x0A
#define PWR_MAN_MAX_CHG_V_REG 0x0C
#define PWR_MAN_MIN_SYS_V_REG 0x0E
#define PWR_MAN_INP_CURR_REG 0x0F

#include <Ponoor_L6470Library.h>
#include <SPI.h>
#include <Wire.h>

// debug serial port
HardwareSerial Serial1(PA10, PA9); // RPi connector
// stepper motor drivers
AutoDriver Stepper1(1, CS_PIN, STEP_RST_PIN, STEP1_BUSY_PIN);
AutoDriver Stepper2(0, CS_PIN, STEP_RST_PIN, STEP2_BUSY_PIN);
// PWM channels
HardwareTimer *PwmPsol, *PwmBlowerCtrl;

void setup() {
  // indicator LED
  pinMode(LED_PIN, OUTPUT);
  digitalWrite(LED_PIN, HIGH);

  // pulse buzzer at beginning
  pinMode(BZR_PIN, OUTPUT);
  for (byte i = 0; i < 20; i++) {
    digitalWrite(BZR_PIN, HIGH);
    delay(1);
    digitalWrite(BZR_PIN, LOW);
    delay(1);
  }

  // debug-serial setup
  Serial1.begin(9600);

  // SPI setup
  digitalWrite(CS_PIN, HIGH);
  pinMode(CS_PIN, OUTPUT);
  SPI.beginTransaction(SPISettings(10000, MSBFIRST, SPI_MODE0));
  SPI.setMISO(PA6);
  SPI.setMOSI(PA7);
  SPI.setSCLK(PA5);
  SPI.begin();

  Serial1.println("Done setting up SPI");

  // I2C setup
  Wire.setSDA(PB9);
  Wire.setSCL(PB8);
  Wire.begin();

  Serial1.println("Done setting up I2C");

  // PWM setup
  PwmPsol = new HardwareTimer(PSOL_TIM);
  PwmBlowerCtrl = new HardwareTimer(BLOWER_CTRL_TIM);

  Serial1.println("Done setting up PWM");
}
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

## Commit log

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2020-04-25 swapped for locking power connector (#37), prep for manufacturing
    [Power.SchDoc, RespiraWorks Ventilator Rev 1.PcbDoc, Watchdog.SchDoc]
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2020-04-25 creating RC2 to correct #53
    [20200424v2-RespiraWorks-Ventilator-Rev1.0-RC2-ASSY-BOM.xls, Power.SchDoc]
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2020-05-17 Updates general README with new structure + couple other fixes
    [[Flow Measurement Venturi - 10-32 Style] v3.iges, [Flow Measurement Venturi - 10-32 Style] v4.f3d]
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2020-05-19 updating comments and fixing compile issues with reference design import
    [Alarms.SchDoc, Cycle-Controller-Onboard.SchDoc, RespiraWorks Ventilator.PrjPcb, ST-LINK.SchDoc]
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2020-05-27 fixed directory case
    [venturi-3-4.f3d, venturi-3-4.iges, venturi-5-8.f3d, venturi-5-8.iges]
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2020-06-02 Updates folder names for project-venturi & pneumatic-system to fix root readme broken links
    [venturi-3-4.f3d, venturi-3-4.iges, venturi-5-8.f3d, venturi-5-8.iges]
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2020-07-20 Adds consolidated CoVent links to root README
    Puts software in its own folder; Updates root README
    Moves system-design folder contents into repo root
    adds pre-commit formatting
    Fixes borked links
    fixes more borked links
    Converts PCBreathe & SysDesign repo links
    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
    [flow-test-21818rpm.csv, flow-test-24000rpm.csv, flow-test-26666rpm.csv, system-reqs.xlsx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]
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2020-08-08 DNP'd C33 and C34 per issue 846 (#848)
    * DNP'd C33 and C34 per issue 846
    * removed broken ephemeral ebay link
    [RespiraWorks Ventilator.PrjPcb, Switches.SchDoc]
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2020-08-22 "removed obsolete exports; updates #873"
    "more restructuring; updates #873"
    "fixed some links; updates #873"
    "a picture and more cross-links; updates #873"
    "added link to last point with old versions of PCB; updates #873"
    [20200423v3-REVIEW-RespiraWorks-Ventilator-ASSY-BOM.xls, 20200424v2-RespiraWorks-Ventilator-Rev1.0-RC2-ASSY-BOM.xls]
2020-08-27 "moved things around; updates #875"
    "fixed dead links; updates #875"
    "fixed a whole bunch of links; updates #875"
    "more link fixes, removing references to pcbreathe; updates #875"
    "updated pictures and beta page; updates #875"
    "pizza, enclosed builds updated, graphics cleaned up; updates #875"
    "fixed some links from main page; updates #875"
    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
    [flow-test-21818rpm.csv, flow-test-24000rpm.csv, flow-test-26666rpm.csv, venturi-3-4.f3d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]
2020-09-04 md conversion of design overview; updates #801
    split the covent overview doc and moved files accordingly; updates #801
    rewrote pneumatic design docs; updates #801
    revamped electrical system page; updates #801
    revamped software design docs; updates #801
    converted covent status update to md; updates #801
    added the rest of the stuff from the covent status report, deleted PDFs; updates #801
    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
    [venturi-5-8.f3d, venturi-5-8.iges]
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2020-11-04 updates #806 Updated pneumatic diagram and stubbed out page for oxygen subsystem under manufacturing Added content about oxygen subsystem, oxygen sensor and oxygen sensor manifold Updated simple test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
    [Reducer 1-4in x 3-4in.ipt, oxygen_sensor_manifold.ipt, venturi-3-4.f3d, venturi-3-4.iges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]
2020-11-19 # This is a combination of 2 commits. # This is the 1st commit message:
    Redesigned filter housings in Inventor.
    Added *.iam (Inventor assembly files) to LFS
    updates #917
    # This is the commit message #2:
    Filter housing updates
    Config files for Siraya Clear blue 2
    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
    [Filter assembly.iam, Filter cover.ipt, Filter gasket.ipt, Filter housing.ipt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]
2020-11-19 Redesigned filter housings in Inventor. Added *.iam (Inventor assembly files) to LFS Filter housing updates Config files for Siraya Clear blue 2 Updated instructions and illustrations for filter hous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
    [Filter assembly.iam, Filter cover.ipt, Filter housing.ipt]
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2020-11-24 Added blower mounting drawings file naming convention for blower assembly assets Added blower subassembly Instructions. cleaned up file structure for blower assembly, naming and minor fixes in doc re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
    [blower_gasket.dxf, blower_holding_plate.dxf, driver_mounting_plate.dxf, tubing_adapter.sldprt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]
2020-12-01 Inceptionev/archive pcb altium project (#920)
    * archiving altium project
    * corrected links
    * delete unnecessary file
    * moved rev A WIP archive inside rev1_export
    * update for #920 readme change request
    * Update README.md
    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
    [Alarms.SchDoc, Cycle-Controller-Onboard.SchDoc, Cycle-Controller.SchDoc, Power.SchDoc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]
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2020-12-21 Alarms, low-voltage power
    Added alarms
    Added alarm battery handling inc. low-battery detection and swap-over from +5V power
    Added 3.3V regulators
    Consolidated some resistor values in 5V buck and fixed BOM elsewhere
    [Ventilator.sch, alarms.sch, cycle_controller.sch, driver_solenoid.sch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]
2020-12-23 Fixed programmer
    Added missing connection from pin 26 to SWCLK (CC_SWCLK_Out)
    [stm_programmer.sch]
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2021-01-10 Pressure sensor + RTC changes
    Added ~enable output to blower connector, changed connector
    Misc. adj. to blower ctrl connector to work with all candidate blowers
    Replaced discrete level shifter for blower
    Added optional PWM filter to blower ctrl for generating analog ctrl voltage
    Added mechanical footprints for pressure sensor daughterboards
    Linked footprint for RTC's battery holder
    [Ventilator.sch, misc.sch, sensors_pressure_daughterboard.sch, sensors_pressure_daughterboard_i2c.sch]
2021-01-11 swapping RTD for NTC circuit. Added gain clarifying notes on Oxygen sensor circuit.
    [sensors_o2_temp.sch, sensors_temp_ntc.sch]
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2021-01-24 PCB Rev A: Switch ~Signal inversion to nSignal inversion (#984)
    * adding system monitor ADC
    * adding system monitor ADC
    * DNP'd external reference and added 0-ohm option resistor to tie VREF to 3.3V supply
    * first commit
    * Initial commit
    * adding system monitor ADC
    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
    [Ventilator.sch, alarms.sch, cycle_controller.sch, driver_solenoid.sch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]
2021-01-26 Created the Inventor part files, 2D drawings, and DXF files and placed them in a newly created pneumatics/CAD folder Ventilator Enclosure Panel files added: Ventilator Enclosure ipt added, six folds 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
    [IS 2907 - 1961 - 3 x 14 x 8.6.ipt, enclosure_assembly.iam, equipment_bracket.ipt, ventilator_closure_panel.idw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]
2021-01-26 Pinch valve migration to Inventor: added NEMA17 model to pinchvalve CAD pinch valve base redesign in Inventor, rotor design fundamentals pinch valve assembly complete minor tweaks and better parametr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
    updates #941
    [NEMA17.ipt, Pinch valve assembly.iam, Pinch valve base.ipt, Pinch valve rotor.ipt]
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2021-01-31 Oxygen sensor manifold modifications, updates #780 enlarged tube length, added loc for NPT more modifications, added boss for NPT fitting Added 1/4 NPT, elongated tubing, drawings, and updated readme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
    [Reducer 1-4in x 3-4in.ipt, oxygen_mixer.ipt, oxygen_relief_assembly.iam, oxygen_relief_manifold.idw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]
2021-02-01 Migration of Blower Components to Inventor and Addition of Engineering Drawings (#931)
    * Added .ipt of tubing adapter;
    Added tubing adapter link to ReadMe, added blower holding plate.ipt
    readme actually updated this time!
    Added tubing adapter drawing
    * Added tubing adapter drawing pdf to readme, reformatted tubing adapter section to remove solidworks files. Added blower holdign plate drawings and inventor files, added to readme
    * Added tubing adapter holding plate .ipt, .idw, and pdf to readme, replaced image with drawing
    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
    [Dummy Pnuematics Tray.ipt, blower_assembly.iam, blower_assembly.idw, blower_driver_ws1208.ipt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]
2021-02-02 v0.3 Face plate redesign (#983)
    * Upper and lower acrylic face plate related part file, drawing, PDF and DXF added
    * upper and lower face plate redesigned and related files added
    * Changed corner mounting holes of upper and lower face plates to allow for M4 nuts, same as pneumatic tray mounting to enclsoure tray. Added .stl files for both as well; updates #938; updates #937
    * dxfs excluded from precommit trailing whitespace checks; bad links in filter holder page fixed
    * Editable part files recreated in Inventor; updates #938
    * Some minor readme changes and updates to the drawing file; updates#938
    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
    [DisplayAssembly.iam, Dummy Pnuematics Tray.ipt, Filter assembly-01.iam, Filter assembly-02.iam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]
2021-02-03 Venturi Configurations CAD Modeling and Drawings (#1009)
    Venturi updates for pneumatic assembly adaptation
    * Created configs for oxygen and inhale venturis; updates #1008
    * added exhale venturi config, updates #1008
    * made drawing, created assembly configs; updates #1008
    * Added links to redame, new drawing files and assembly model; updates #1008
    * "readme formatting bugs; updates #1008"
    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
    [venturi-exhale.ipt, venturi-influx.ipt, venturi-o2.ipt, venturi-pizza.ipt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]
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

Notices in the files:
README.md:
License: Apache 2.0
